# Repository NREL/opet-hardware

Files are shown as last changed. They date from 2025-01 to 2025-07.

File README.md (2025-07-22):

# OPET hardware introduction
This repository contains everything relating to the hardware of the OPET device.  If you are looking for the firmware or software repositories, links are below:

[OPET Firmware](https://github.com/NREL/opet-firmware)

[OPET Control Software](https://github.com/NREL/opet-control)

## Feature summary
- OPET (Open-source Photovoltaic Electrical Tool) is used for performance measurements of solar photovoltaic (PV) devices in the field under natural sunlight or in the lab under artificial light
- Its primary use is in research and development of solar cells and modules, specifically in reliability and durability research of PV devices
- Some features and functions include:
    - IV curve measurements with linear or cosine distributed measurement points
    - PV device active loading at open circuit voltage (V<sub>oc</sub>), short circuit current (I<sub>sc</sub>) and maximum power point (P<sub>mp</sub>)
    - Bias power supply to overcome series resistance in contact wires for I<sub>sc</sub> measurements and loading
    - PV voltage input in five ranges from 1V to 100V
    - PV current input ranges
        - Low current version, six current ranges from 1.1mA to 340mA
        - High current version, six current ranges from 50mA to 15A
    - IO ports for I2C and SPI temperature sensor Arduino extension boards
    - Integrated fan control

## Safety note

## General Specifications
- Input Power
    - Amplifier supply: 24 Vdc nominal (19 Vdc -- 29 Vdc)
        - Low Current Version 250mA maximum
        - High Current Version 150mA maximum
    - RS485 supply: 5 Vdc nominal (4.75 Vdc -- 5.25 Vdc), 200mA maximum for entire bus
    - High current OPET PV bias supply: 2.0 Vdc to 5.5 Vdc, 15A maximum
    - Fan relay power feedthrough: 24 Vdc recommended (\<150 Vdc, \<100 Vac), 2A maximum
- Electrical Protection
    - Amplifier supply: 30 Vdc, fused with 500 mA ceramic fast blow 20 mm x 5 mm fuse
    - RS485 supply: 5.6 Vdc, requires external 250 mA inline fuse for RS485 bus
    - PV voltage: 100 V on all ranges
    - PV current, High current OPET PV bias supply: 100 V on all ranges
    - High current OPET PV bias supply and PV current:
        - 15 A on all ranges, fused with 16 A \>100 Vdc rated 32 mm x 6.3 mm ceramic fuse
    - Low current OPET PV current:
        - 340 mA on all ranges, fused with 500 mA \>100 Vdc rated 20 mm x 5 mm ceramic fast blow fuse
        - It should survive at 15A current spike with the correct fuse installed in case a full-sized module is connected to a low current OPET by accident, but not tested yet
- Environment
    - Temperature
        - Operation 0 °C to 40 °C
        - Storage -30 °C to 60 °C
    - Relative humidity (non-condensing)
        - Operating 0 °C to 28 °C \<90 %
        - Operating 28 °C to 40 °C \<80 %
        - Storage -30 °C to 60 °C \<95%
    - Altitude
        - Operating up to 3,000 Meters (limited by PCB track spacing according to ICP 2221)
        - Storage up to 12,000 Meters
- Remote interface
    - RS485 half-duplex, 200k baud, up to 32 devices per bus

## Electrical Specifications

### PV Voltage Specifications
- Maximum input: 100V on any range
- Measurement method: 16bit SAR ADC
- Input characteristics:
    - Range defines the nominal range value; system is designed with a \>3% overrange margin
    - Eff. ADC resolution describes the ADCs effective performance, \~15bit
        - The 1V range is effectively a part of the 4.2V range
    - Accuracy is given as ± (% of measurement + % of range), detailing scale and offset uncertainty respectively
        - The total uncertainty of a measurement is defined as $U = \ \sqrt{{U_{Scale}}^{2} + {U_{Offset}}^{2}}$
        - Uncertainty is reported with a 95% confidence (k=2)
        - Uncertainty is largely based on theoretical calculations, albeit care has been taken to include every conceivable source, these may not be fully representative, design requirement was a total uncertainty of less than 0.1%
        - Uncertainty given excludes external calibration uncertainty, calibration should be caried out using suitable equipment that does not add a significant contribution
    - Input impedance describes the total voltage terminal resistance path when voltage is within selected measurement range, the resulting current leakage is corrected on current measurements taken
    
| Range | Eff. ADC resolution |    Accuracy     | Input Impedance |
|:-----:|:-------------------:|:---------------:|:---------------:|
| 1.0 V |       0.14 mV       | 0.011% + 0.031% |    1.100 MΩ     |
| 4.2 V |       0.14 mV       | 0.011% + 0.007% |    1.100 MΩ     |
| 10 V  |       0.32 mV       | 0.019% + 0.007% |    0.163 MΩ     |
| 30 V  |       0.97 mV       | 0.025% + 0.007% |    0.115 MΩ     |
| 100 V |       3.23 mV       | 0.038% + 0.007% |    0.104 MΩ     |

### PV Current Specifications
- Maximum input:
    - High Current OPET: 15A on any range
    - Low current OPET: 340mA on any range
- Measurement method: 16bit SAR ADC
- Input characteristics:
    - Range defines the nominal range value; system is designed with a \>3% overrange margin
    - Eff. ADC resolution describes the ADCs effective performance, \~15bit
    - Accuracy is given as ± (% of measurement + % of range), detailing scale and offset uncertainty respectively
        - The total uncertainty of a measurement is defined as $U = \ \sqrt{{U_{Scale}}^{2} + {U_{Offset}}^{2}}$
        - Uncertainty is reported with a 95% confidence (k=2)
        - Uncertainty is largely based on theoretical calculations, albeit care has been taken to include every conceivable source, these may not be fully representative, design requirement was a total uncertainty of less than 0.1%
        - Uncertainty given excludes external calibration uncertainty, calibration should be caried out using suitable equipment that does not add a significant contribution
- Current measurements are corrected for leakage through the PV voltage channel impedance

#### Low current OPET
|  Range  | Eff. ADC resolution |    Accuracy     | Shunt Resistance |
|:-------:|:-------------------:|:---------------:|:----------------:|
| 1.1 mA  |       35.1 nA       | 0.050% + 0.017% |     23.20 Ω      |
| 3.2 mA  |      104.4 nA       | 0.049% + 0.008% |     23.20 Ω      |
| 11.0 mA |       360 nA        | 0.056% + 0.017% |      2.26 Ω      |
|  33 mA  |       1072 nA       | 0.055% + 0.008% |      2.26 Ω      |
| 110 mA  |       3.70 µA       | 0.053% + 0.018% |      0.22 Ω      |
| 340 mA  |      11.01 µA       | 0.052% + 0.008% |      0.22 Ω      |

#### High current OPET
|  Range   | Eff. ADC resolution |    Accuracy     | Shunt Resistance |
|:--------:|:-------------------:|:---------------:|:----------------:|
| 50.0 mA  |      1629.0 nA      | 0.059% + 0.017% |      0.50 Ω      |
| 150.0 mA |      4843.6 nA      | 0.054% + 0.008% |      0.50 Ω      |
| 500.0 mA |      16290 nA       | 0.055% + 0.017% |      0.05 Ω      |
| 1500 mA  |      48436 nA       | 0.058% + 0.008% |      0.05 Ω      |
| 5000 mA  |      162.90 µA      | 0.057% + 0.017% |      0.01 Ω      |
| 15000 mA |      484.36 µA      | 0.058% + 0.008% |      0.01 Ω      |

# Preparing for Operation
- The OPET circuit board needs to be prepared and set-up for operation
- First an overview of the OPET printed circuit board (PCB) is given
- it is detailed how to wire up and power the system
- enclosure with air-cooling requirements and recommendations are also given

## Circuit Board overview and outline

### Low current OPET PCB overview


### High current OPET PCB overview


### Dimensions
- Both, low and high current OPET boards have the exact same PCB with a different set of components
- hence, board dimensions and the positions of the mounting holes are the same


### Connectors
- All of the side connectors on the OPET are pluggable screw or clamp terminals
    - This is to reduce the strain on the PCB when connecting a cable
- CAUTION:
    - Always disconnect the pluggable connector before connecting/removing wires from the plug
    - Not removing the plug puts pressure onto the board from the top when tightening or loosening the screw that bends the PCB and can cause micro-cracking in components
    - Early failure especially in capacitors and changes in performance with calibration drift may be result
- The labelling of connectors is done on the front and the backside of the PCB, so that it is easily readable in different mounting positions
- Labelling is as following, see section in 2.2 for further details:
    - Amp PWR: 24V & GND amplifier power supply input
    - RS485: two RS485 communication ports with A & B data lines and 5V & GND supply input
        - One for input and one for feedthrough to the next unit
    - Fan: standard molex fan connector powered from the 24V Amp PWR input
    - FT: fan power feedthrough relay connection to be used with an externally powered fan
    - SPI & I2C ports: these are expansion sockets to connect a breakout module with RTD or thermocouple sensor
    - PV Curr: for the current carrying pair of the 4-wire contacts to the PV device
    - PV Volt: for the voltage sensing pair of the 4-wire contacts to the PV device
    - Bias PWR: for the bias power supply input on the high current OPET version
    - MOSFET: for the external driver MOSFET if not onboard
    - NTC2: for the external driver MOSFET temperature sensor

### Headers, Jumpers and Fuses
- Two headers are positioned in the left area of the PCB with following function:
    - ISP: is the 6-pin In-System Programmer port used to program the microcontroller on the board
    - JTAG: the Joint Test Action Group port is used for debugging and programming of the onboard microcontroller
        - This port is normally disabled to make room for the RS485 address selection
        - Is very useful for updating and finetuning the controller code
        - Make sure ADR jumpers are removed before using this port
    - Both ports follow the standard AVR pin-out and can be connected directly to a programmer
        - an Atmel-ICE programmer has been used during the design of OPET


- The ADR jumper row is used to set the RS485 address of the OPET device

### Fuses
- WARNING:
    - Always replace fuses on the OPET with the correct type and specifications
    - Using the wrong fuse may cause no-functioning protection in case of a fault, which can lead damaged equipment and/or personal injury
- OPET has 2 fuses onboard
    - All Are ceramic fuses, they are used for an improved DC and current braking capability rating
- FS1: amplifier power input fuse
    - 20x5 mm ceramic fuse, 500 mA ≥50 Vdc rated, fast action
    - ideally use "Littelfuse 0216.500MXP"
    - this fuse can blow if the amplifier input voltage is too high and the 30 V Zehner diode protects the input to the DC/DC converters
- FS4: PV device current protection fuse
    - Low current OPET: 20x5 mm ceramic fuse, 250 mA ≥100 Vdc rated, fast action
        - Important to use "Littelfuse 0216.250MXP"
    - High current OPET: 6.3x32 mm ceramic fuse, 15-20 A ≥100 Vdc rated
        - use "Littelfuse 0314015.MXP" 15A fuse or Littelfuse 0314020.MXP" 20A fuse, or "Schurter 8020.5023" 16A fuse
        - IMPORTANT:
            - this fuse is likely to get very hot (\>80°C) when operating at or near maximum specified currents (15 A)
            - hence its recommended to use a 20 A fuse when the PV load is likely to reach near to 15 A current flow, this reduces heat on the OPET board and degradation of the fuse over time (early fuse failure)

### Indicators
- OPET board has 3 indicator LEDs in the left side:
    - Green: Power indicator
        - Indicates if the Microcontroller is receiving 5V input voltage
    - Orange: Output enabled indicator
        - In principle this LED indicates if the output of the OPET is
            - Enabled, driver controller in active voltage regulation
            - Disabled, driver controller inactive with high impedance input (V<sub>oc</sub>) at PV current input
        - Indicator shows enabled if the power output is requested to be enabled
        - In case of an error (see below error indicator details), the actual output can be high impedance inactive, while the output indicator is still active
            - this is to indicate that as soon as the error clears the output will become active automatically
        - in V<sub>oc</sub> load mode, the output is also inactive high impedance, while the OPET shows an output active indicator
            - this is to show that the output is requested to be active and ready to measure IV curves in between V<sub>oc</sub> loading at high impedance
    - Red: Error active indicator
        - This LED will become active when the OPET has detected an error during operation
        - Some errors will lead to a temporal disabling of the output if the output was requested to be on to start with, others are indicative only
        - The type of error that is active can be queried when requesting load measurement data or reading the status byte (see 4.3.1.1 for more details)
        - In case of voltage or current ADC measurement errors the error LED is likely to flash constantly or briefly, if observing this:
            - Check measurement ranges
            - Check stability of PI controller
            - Check noise level on the current and voltage signals
            - Check PV device connection polarity

## Electrical connections and set-up

### Amplifier Supply
- The AMP supply input of the OPET is used to power the electronics on the PCB
    - On the Low current OPET version it also sources the Bias voltage through a DC/DC converter connected to the AMP supply input
- The nominal voltage of the input is 24V, with an input range of 19-29 V
    - Can be powered with a 24V battery system, however it needs additional battery management and protection as OPET will not automatically switch off when it reaches under-or over-voltage conditions
- Normal current draw is \~60-75 mA if the output is off
    - Low current OPET versions can have up to \~150 mA current draw at maximum current PV load
- The AMP input has following protections:
    - reverse polarity protection
    - over-voltage protection with a 30V Zehner diode
    - and fused with a 500 mA 20x5 mm ceramic fuse,
        - Ceramic fuse is used to reach an improved DC and current braking capability rating
- The AMP input is also Isolated, to the rest of the electronics excluding the fan using isolated DC/DC controllers
    - This reduces problems occurring due to ground shifting when connecting multiple OPET boards on to one supply
- OPETs have an AMP input filter and DC/DC output filter to reduce noise impact, it is however still recommended to use a high-quality supply with low output ripple noise
- When selecting a power supply, it is also important to make sure its maximum capacitive load requirement is above the input capacitance of the OPET PCBs (\~25µF) multiplied by the number of boards connected

### RS485 Bus Communication
- OPET incorporates an isolated half-duplex RS485 port for communication
- Up to 32 devices can be connected to a single RS485 bus
    - OPET is designed for 32 devices on one bus, this has not been fully tested
- OPET has two connectors for RS485 onboard
    - one for the RS485 input and one to feedthrough to the next device on the bus
    - both can be used for either function
- To connect OPET devices to a computer it is recommended to use a USB to RS485 converter, devices have been tested with the FTDI USB-RS485-WE-1800-BT USB to RS485 converter
- Following connection schematic is used to connect the OPET systems to a RS485 bus



#### Bus Power Supply
- Since an isolated RS485 system is used to electrically separate multiple devices from each other and to reduce interference the RS485 must be powered with an external 5V supply with a minimum current output of 250mA
- This is in many cases is already incorporated into the USB-RS485 converter, such as with the recommended converter given in the section above, if not, the RS485 bus can be powered with an external supply
- power is feed through from device to device in the same way as the data lines
- The input voltage must be within the range of 4.75 V and 5.25 V for the RS485 transceiver on the OPET to work correctly
- The input is reverse polarity protected and has a 5.6V Zehner clamping diode to protect against short time overvoltage spikes at the input to the transceiver.
    - Short time: maximum a few seconds dependent on the input voltage, fault current and heat on the Zehner diode
    - A 250 mA fuse in line with the RS485 bus power is recommended to enhance protection
    - Current may be electronically limited when using a USB to RS485 converter with 5V output powered via USB, a fuse is in this case not needed
    - If an external dedicated power supply is used to power the RS485 bus is advised to use a 250 mA series fuse in the 5V line to the first OPET device.
- Since up to 32 OPET devices are connected in series via the feedthrough connections and hence the total length of the bus cable can be long, it is advised to use as large wire gauge as possible to reduce the voltage losses within the bus to less than 0.15 V on a 5 V bus input to stay within the transceiver operating voltage range from the first to the last device on the bus while still allowing for input voltage tolerances
    - Total length: keep as short as possible to reduce losses
    - Wire gauge: OPET connectors accept 20 to 26 AWG, the thicker the conductor the lower the losses

#### RS485 bus termination and biasing
- To improve communication reliability and quality the RS485 bus uses termination and biasing techniques
- RS485 bus termination is used to reduce/eliminated signal reflection at the end and start points of the bus
    - Done by connecting a 120 Ω resistor at each end of the bus in series from data A to data B
    - The recommended FTDI USB to RS485 converter has this incorporated and just needs shorting of the dedicated wires to enable 120 Ω termination at the bus start point
    - The OPET device does not have a termination onboard and a external 120 Ω resistor should be connected to the feedthrough terminal (whichever connector is not used yet) of the last device in line from contact A to B
    - a termination is typically not needed on very short bus line (\<2m) with only a few devices connected
- RS485 bus biasing is used to keep the voltage potential of the data lines A & B apart from each other when the bus is inactive and none of the devices on the bus are transmitting
    - Too little biasing can cause accidental start pulses on the bus and interrupt communication
    - OPET has biasing resistors included that allow for optimal biasing at 32 devices on the bus (68 kΩ per device, \~2.1 kΩ in total with 32 devices on the bus)
    - External biasing when not using 32 devices is usually not needed, however if using an old RS485 transceiver (USB to RS485 converter or similar) this may be need when communicating to only a few devices
    - If communication is in the above case unreliable / not working at all do following:
        - At the start of the RS485 bus before the first device connect
            - a 10 kΩ resistor from Data A to 5V
            - and a 10 kΩ resistor from Data B to GND

#### How to set the hardware bus address 
- The bus address of each OPET device is determined by hardware addressing on the PCB, which is the jumper header next to the RS485 connectors
- Any device can have any bus address independent of its position on the actual RS485 bus as long as the address is not used twice
    - In case of using a bus address twice, communication to this address will fail as two devices will start using the bus at the same time
    - OPET does not recognise bus communication collisions when multiple devices communicate at the same time, nor does OPET have an auto-addressing function
- To set the address of a OPET do the following:
    - Insert a jumper into the positions required that make up the desired address number in binary code
    - Address = 1\*x + 2\*x + 4\*x + 16\*x, while x represents a 1 if jumper is inserted and 0 if not
    - Addressing starts at 0 and ends at 31, for a maximum of 32 devices
- IMPORTANT:
    - Remove the Address jumpers when using the OPET in debug mode with a JTAG
    - The default address when debugging is "1" `A:...`
    - See the software programming notes for more details

### FAN and FT connectors
- The FAN connection uses a standard molex connector for computer fans
    - It is powered by the AmpPWR supply; hence it is recommended to use a 24V fan
    - Fan power is not in-line with the amp power fuse
    - up to 2A current rating limited by the control relay
- The FT connector is a relayed power feedthrough that closes when the fan is controlled on
    - This can be used to power fans from an additional power supply
    - Voltage rating is \<150 Vdc, \<100 Vac, 2A current rating
- The fan control is a simple on/off control
    - controlled either manually or automatically (by default) by temperature and load power hysteresis that can be configured in the EEPROM (see section 5.3.19)

### SPI and I2C ports
- The SPI and I2C ports can be used to connect breakout board to the OPET
- Main use is to connect temperature sensor breakout boards
- OPET currently supports following boards:
    - Adafruit MCP9600 I2C Thermocouple Amplifier
        - Connected directly to J8
    - Adafruit MAX31865 RTD PT100 or PT1000 Amplifier
        - Connected directly to J18
    - See section [XXX]{.mark} for details on how to configure a temperature sensor breakout board
- IMPORTANT:
    - Switch off the OPET before disconnecting or connecting a breakout board
- The pinout description is given on the OPET PCB and below

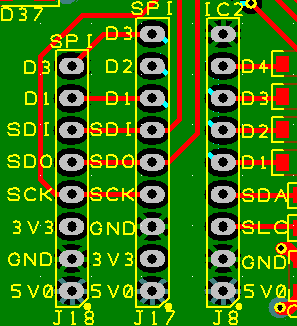
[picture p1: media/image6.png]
Pinout description of the OPET I2C and SPI expansion ports


### High Current OPET Driver Stage and Voltage Bias Supply
- WARNING:
    - Do not connect/ disconnect test leads from the bias voltage supply to the OPET when it is under load or when the PV device is placed under light and supplying electricity
    - Do not connect/ disconnect test leads from the driver MOSFET to the OPET when it is under load or when PV device is placed under light and supplying electricity
    - Cover the module with cardboard or similar to remove light input and power off OPET when connecting / disconnecting test leads
- The driver MOSFET and bias voltage protection diodes are mounted externally on a heatsink due to the additional heat produced from the larger load and current flow
- The bias voltage supply is also external, as it needs to supply the same current as the PV device
- Due to the low load current and total heat dissipation, those components are internal on the low current OPET versions
- The bias voltage supply is connected with two protective diodes:
    - One diode in series for reverse polarity protection
    - And one diode in parallel to bypass the voltage supply in case it is switched off or cannot keep up with the PV device load current
    - The "onsemi FFPF30UP20STU" diode is recommended
        - due to its low forward voltage even at high currents (typically 0.9 V at 15 A)
        - due to its isolated case, meaning no thermal pads are needed, only thermal paste, which improves thermal conductivity significantly
- the requirements of the bias voltage power supply are as follows:
    - output voltage minimum 0 V (just shorted) to maximum 6 V
        - dependent on the length of the cable to the PV device and the maximum current flowing
        - the losses on the cables, protection diode and within the OPET board must be lower than the voltage bias supply to be able to measure directly at I­<sub>sc</sub> load
        - if the bias voltage is too low, the OPET system will not be able to get to I<sub>sc</sub> loading at the PV device, which may be less of a problem with high voltage PV modules, but will cause problems when measuring wafer sized solar cells
    - output current of at least the expected maximum current of the PV device
        - a reserve headroom of \~30% is recommended
        - if the PV load current exceeds the bias voltage supply current, the current is bypassed through the protective diodes, meaning the OPET will not be able to reach I<sub>sc</sub> load
    - use a power supply with the lowest noise possible, as this will improve measurement quality and stability
        - unlike the low-current OPET version with bias supply on-board, the high current version has no bias voltage supply filter
        - a noisy voltage supply will cause noisier PV load measurements
    - when using a single bias voltage supply for multiple high current OPETs:
        - connect them using a star connection directly to the power supply terminals, as this will reduce voltage loss and reduce board to board noise coupling
        - use protective diodes for each board separately, to prevent PV load power flow from one board to another
- The driver MOSFET is connected to the MOSFET input of the OPET
    - The "IXYS IXFN132N50P3" MOSFET is recommended
        - Due to its high current and voltage load capability
        - Due to its large metal base footprint and ability to sink up to 1.5kW of power
        - Due to its isolated base, meaning no thermal pad is needed, only thermal paste, which improves thermal conductivity significantly
    - Is its recommended to use one driver MOSFET only, but multiple can theoretically be used
        - This can increase the practical maximum load
        - however, comes with additional difficulties, see end of this section for recommendations
- A NTC thermal sensor is additionally mounted onto the MOSFET and connected to the OPET, to make sure the system does not overheat
    - Recommended NTC is the "EPCOS B57703M0103A018"
        - Has through hole mounting and comes wire leaded
- Refer to section 2.3.3 for details and requirements to mount the MOSFET and diodes on a heatsink
- Wire requirements are as follows:
    - MOSFET and Bias voltage connectors accept 12 to 24 AWG
    - The thicker the conductor the lower the losses induced by wire resistance and current flow
    - The MOSFET should be connected using the shortest wiring possible, as long cables may introduce high stray capacitance and inductance on the MOSFET gate that reduce driver stability
    - The Bias Voltage protection diodes should also be as near as possible to the OPET, but this requirement is less important
- Following connections need to be made to connect the driver MOSFET and bias voltage with protection diodes:


- Using multiple driver MOSFETs (untested):
    - Use the same type of MOSFET for all
        - Need to be able to sink the current and voltage each, as per datasheet
    - Need to be mounted onto the same heatsink with as good as possible thermal coupling
        - Temperature differences can cause a thermal runaway that cause the hottest MOSFET to carry even more load, heating it further, possibly leading to failure
        - If one MOSFET overheats and fails, all are likely to fail in a cascading failure
        - Thermal coupling can reduce the imbalance between MOSFETs significantly
    - MOSFETs need to have each a separate gate resistor of \~100 Ω (needs testing)
    - MOSFETs must be wired with equal length cables to OPET in a star configuration
        - This reduces imbalance due to series resistance in cables
    - Ideally test the on-resistance of all MOSFETs and use those with most similar on-resistance
        - So called binning
        - Reduces imbalance due to series resistance
    - NTC must be mounted to the MOSFET that is most likely to get hottest (may need additional testing)
    - Below is a diagram of wiring multiple driver MOSFETs to the high-curent OPET



### PV device Connections
- WARNING:
    - Do not connect/ disconnect test leads from the PV device to the OPET when it is under load, or it is in placed under light and supplying electricity
    - Cover the module with cardboard or similar to remove light input when connecting / disconnecting test leads
- PV device connections are made using 4 wires, 2 for the PV device current and two for the PV device voltage sense
    - The pair of current wires carry the current load with low impedance
    - The pair of voltage sense wires have a high input impedance at the OPET and therefore sense the PV voltage without additional current induced voltage losses
    - the voltage is measured at the PV device compensating for losses due to long test leads
- Wire requirements are as follows:
    - PV current connector accepts 12 to 24 AWG
        - the PV current cables should be as short as possible
        - the shorter the lower the losses and bias voltage requirements, the less noise pick-up and the better the stability
    - PV voltage connector accepts 16 to 28 AWG
        - The PV voltage cable should be shielded 2 core to reduce noise pick-up
        - Cable shield should be connected to S (Shield) of the PV volt connector



## Enclosure and cooling
- The printed circuit board (PCB) needs to be housed in an electrically safe enclosure that adequately protects from electric shock and personal injury
- Furthermore, forced air cooling is required for reliable operation within specifications

### Enclosure
- Ideally a metal housing should be used with earth grounding for safety and to reduce signal noise influences
- Mounting of the board can be done vertically in PCB guiderails or horizontally using the mounting holes
- System can be mounted in 19" rack units with multiple units next to each other
- See PCB design notes for mounting hole positions

### Circuit board air cooling
- Active cooling and ventilation of the PCB is required especially when operating the OPETs at high PV device current / power, it has following impact on the system:
    - it improves measurement stability as the board and shunt resistor heatsink temperatures are lower and vary less with PV device load current and power
    - it improves reliability the driver MOSFET and other components
    - it reduces aging drift in the shunt resistors and thus increases stability
- The low current OPET can be used without air cooling if the total power of the PV device does not exceed \~3W
    - cooling should be used above 3W and is a must above \~5W, as otherwise the heat sink will get too hot and trigger the thermal cut-off
- the high current OPETs need separate cooling for the circuit board and for the heatsink with the driver MOSFET and protective diodes
    - high PV currents induce heat on the PV current protection fuse and on the shunt resistors
    - the driver MOSFET carries the electrical load of the PV device and thus must be operated with a good heatsink (see the following section)
- the Airflow should be from front to back of the OPET boards or from bottom to top
    - this makes sure that the heatsink of the shunt resistor is cooled first and secondly the drive MOSFET heatsink or PV current fuse
    - basically, air needs to flow first past measurement critical components and then past power electronics, so that measurement components do not get unnecessarily heated

### High current OPET driver MOSFET and diode cooling
- due to the high current and power potentially going through the high current OPET boards, the driver MOSFET and the bias voltage protection diodes are external from the PCB
- those must be mounted onto a suitable heatsink that is able to take the maximum predicted power from the PV device plus the power from the bias voltage supply
- total estimated power can be calculated as follows:

$$P_{total} = P_{MP} + (V_{bias} - V_{Diode} - V_{cable})*\ I_{MP}$$
- cooling option can either be water or air cooling
- the best cooling option depends on the maximum power requirements
    - with 100 V and 15 A measurement range, theoretically a 1.5kW PV load can be connected
        - Is unlikely practically possible with a PV device
        - a single driver MOSFET load set-up of any kind will probably go off in smoke at this point
    - the maximum load depends mostly on the thermal resistance path from the junction of the driver MOSFET to the heat removing medium (Water, Air)
    - the maximum MOSFET junction temperature should be well below its allowed maximum for reliability (maximum \~100 °C for at 150 °C maximum allowed operation temperature)
    - the temperature of the heat removing air/water influence maximum power as well
- it is important to take care when mounting the MOSFET and protection diodes
- the MOSFET should be mounted as following:
    - in the centre of the heatsink with high grade thermal compound in between heatsink and MOSFET
    - do not use thermal pads, as they have lower thermal conductivity and thus can cause excessive heat at the MOSFET that can reduce lifetime or burn it instantly
        - the recommended MOSFET "IXYS IXFN132N50P3" has an isolated metal base, hence additional electrical isolation is not needed
    - mount the thermistor temperature sensor (NTC) directly onto the MOSFET with its mounting screws that go into the heatsink
        - the NTC is the lifeline of the driver MOSFET as it means the OPET can monitor the case temperature and shut power of before damage occurs
        - the NTC head must be mounted between the screw head and MOSFET base
        - Do not mount the NTC between the heatsink and MOSFET, as this will cause a thermal gap and certain death of the MOSFET
- the diodes (recommended "onsemi FFPF30UP20STU") should also be mounted at a distance to the MOSFET using thermal compound
    - thermal pads are not needed due to an isolated TO-220F case
- a suitable heatsink for air cooling is for example the "Fisher Electronik LA 17/150 24V or LA 17/200 24V ", were the 24 Vdc fan option should work best
    - it is estimated that this heatsink should allow for a PV load of \~350 W based on a total thermal resistance of 0.20C/W, reaching a MOSFET junction temperature of \~100 °C at 25 °C air temperature
        - 0.07 °C/W for heatsink, 0.083 °C/W MOSFET junction to case, 0.05 °C/W MOSFET case to heatsink
    - Estimated 12 A maximum current with a 2 Vdc bias voltage remaining after diode and cable losses, causing 24W additional heat at MOSFET
    - It remains to be tested in real operating conditions, as the total thermal resistance may be too optimistic, due to the relatively small surface area of the MOSFET connecting to the heatsink

## Turning Power-On
- After adhering to the endless list of requirements, warnings & cautions, boxing it all in and hocking up the cables, one should be able to just power it up and get going
- The OPET system boots up and is ready to go in less than a second
    - WARNING:
        - it may also go up in flames just as fast as it boots
            - if it is powered by direct mains voltage
            - if it is not wired correctly
- To power up the OPET only amp power is needed, there is no strict on/off button, it powers up as soon as power is connected and will stay powered up until the input power is removed
    - If a power button is desired, a switch can be added to the positive pole of the AMP input power line

# Calibration

## Introductions
- Following sections detail the calibration and adjustment procedure for the OPET systems
- Care should be taken to make sure measurements are done without introducing additional errors
- Furthermore, take note that the high current and low current versions of the OPETs require different current calibration connections!
- The easiest way to calibrate the OPET devices is to use the calibration software tool developed for it, however this only works with a Fluke / Wavetek 9100 calibrator at the moment
- WARNING: make sure the calibration set-up is electrically touch prove and save, as the calibration will source voltages over 42 Vdc into the OPET devices, which can result in personal injuries or death if accidently touched

## Requirements
- A current and voltage calibrator should be used to calibrate the OPET system
- For this a controllable power supply in combination with a digital multimeter can also be used
- Important is that the measurement uncertainty of the calibration system is lower than that of the OPET devices
    - The total uncertainty is the OPET (see section 1.4) uncertainty combined with the calibration uncertainty
    - if calibration uncertainty is high, the resulting uncertainty after calibration and adjustment will degrade OPET total uncertainty
- calibrations have been down using a Fluke / Wavetek 9100 calibrator, for which also an easy-to-use calibration tool was developed
    - this requires a GPIB connection the calibrator and the computer
    - and a LabVIEW 2018 32bit runtime install to run the executable (or a licence to open/run the VI files)
- WARNING, it is important to shield the OPET during calibration:
    - Foremostly, to make sure it is electrically safe and high voltage parts cannot be touched
    - Secondly, a metal case to reduce measurement noise
        - An earth wire may be used to connect to a metal case
        - The shield input at the PV voltage terminals can be used connect case and OPET
        - it may take a little tinkering to get the best results with lowest noise
- otherwise, all you need is luck, patients and suitable connections with calibration cables

## Calibrator Connections

### Voltage
- Voltage calibrations are carried out by making a 2-wire connection between the calibrator voltage terminals and the PV voltage input terminals
- Since the OPET voltage input is differential to provide 4-wire PV measurements, the negative PV terminal and the shield input of the PV voltage connector should be bridged
    - This should reduce signal noise significantly
- Following connection diagram was used for high and low current OPET devices:


### Current
- Current calibration connections are not made via the PV current input terminals on the OPET devices due to the driver MOSFET and the bias voltage supply that is in line with the PV current terminals
    - Instead, current calibration is done with connections going directly over the shunt resistors current path, bypassing the drive MOSFET and the bias voltage supply
    - Using the PV current terminals may be possible, but has not been done as it may risk damaging the calibrator
- CAUTION:
    - Low and high current OPET devices use different current calibration connections
    - Do not use the low current connections for calibrating OPETs with more than 150mA current
    - Doing so will likely result in damaging the OPET

### Low Current systems
- Following connection diagram is used for the low current OPET devices

- The connections for calibrating the low current devices are done from the current outputs of the calibrator to the OPET device
    - Negative pole: PV voltage connector shield (S) terminal
    - Positive pole: MOSFET connector source (S) terminal
- CAUTION: do not use the low current connections for high current calibrations above 350mA
    - This may result in damaging the OPET PCB by burning off the voltage terminal shield track which cannot handle high currents, even for short times

### High Current systems
- Following connection diagram is used for the hight current OPET devices
- This configuration can also be used for low current OPET devices if the bias connector is installed or one connects directly to the PCB at the Bias PWR GND terminal


- The connections for calibrating the high current devices are done from the current outputs of the calibrator to the OPET device
    - Negative pole: Bias power connector ground (GND) terminal
    - Positive pole: MOSFET connector source (S) terminal
- The bias voltage supply ground connector can handle high currents
    - hence this terminal is used for high current OPETs
    - it can also be used on low current units, but the connector may not be installed

# Making OPETs

## PCB Design Files
The provided files were created using [RS Design Spark](https://www.rs-online.com/designspark/pcb-software) software.  Schematics of individual systems are broken out individually.  The PCB design is unified between both the HC and LC versions of the OPET.  Custom library components are also provided.

[OPET PCB Design Files](OPET_PCB_Design_Files)

Note that bills of materials for board components are located in the [OPET Manufacture Files](OPET_Manufacture_Files) folder.

## Manufacture Files
If your goal is to just have some OPET tools manufactured, all the necessary files are included in the [OPET Manufacture Files](OPET_Manufacture_Files) folder.  These files should include everything a PCB manufacturing house needs to fabricate the PCBs and acquire and assemble components.

- **OPET - Gerber** Gerber manufacturing files.
- **OPET - BOM Hardware** List of mechanical hardware options for assembling OPETs.  This includes things like screws, nuts and thermal pads or paste.
- **OPET - BOM HC** Bill of materials for the high current OPET model.
- **OPET - BOM LC** Bill of materials for the low current OPET model.
- **OPET - CPL Component Placement List** Contains the positions and orientations of components.  Will be required for PCB assembly.
- **OPET - PCB Manufacturing Notes** Includes notes about copper weight, board specifications and other notes that a manufacturer will need.

# Disclaimer

DISCLAIMER: NREL/ALLIANCE FOR SUSTAINABLE ENERGY, LLC/DOE DISCLAIM ALL WARRANTIES, EXPRESS OR IMPLIED, INCLUDING THE WARRANTIES OF MERCHANTABILITY OR FITNESS FOR A PARTICULAR PURPOSE, AND MAKES NO WARRANTY AS TO THE ACCURACY, COMPLETENESS, OR USEFULNESS OF ANY INFORMATION PROVIDED HEREIN. USE OF THIS PACKAGE IS AT THE USER’S OWN RISK.

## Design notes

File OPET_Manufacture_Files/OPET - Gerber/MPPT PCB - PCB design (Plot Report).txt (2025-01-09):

Plot Report
-----------

Report Written:     Wednesday, May 15, 2024
Project Path:       D:\BLISS_DATA\7_WORK_SPACE\NREL MPPT tracer\Hardware\OPET PCB\MPPT PCB - Project.prj
Design Path:        D:\BLISS_DATA\7_WORK_SPACE\NREL MPPT tracer\Hardware\OPET PCB\MPPT PCB - PCB design.pcb
Design Title:       
Created:            03/04/2020 02:22:14
Last Saved:         15/05/2024 23:10:25
Editing Time:       25039 min
Units:              inches (precision 4)

Device Settings
===============

Gerber Settings
===============

    Leading zero suppression.
    G01 assumed throughout.
    Line termination <*> <CR> <LF>.
    3.5 format absolute inches.

    Format commands defined in Gerber file.
    Aperture table defined in Gerber file.
    Hardware arcs allowed.

Drill Settings
==============

    Excellon Format 2
    Format 3.5 absolute in inches.
    Zero suppression Leading

Plots Output
============

    Plot Job: "D:\BLISS_DATA\7_WORK_SPACE\NREL MPPT tracer\Hardware\OPET PCB\MPPT PCB - PCB design.mop"

Gerber Output
=============

D:\BLISS_DATA\7_WORK_SPACE\NREL MPPT tracer\Hardware\OPET PCB\Gerber\MPPT PCB - PCB design - Top Silkscreen.gbr

    Layers:
    ------------------
    Top Silkscreen

    D-Code Shape  (thou)
    -----------------------
    D10    Round 5.00
    D76    Round 10.00
    D77    Round 12.00

Gerber Output
=============

D:\BLISS_DATA\7_WORK_SPACE\NREL MPPT tracer\Hardware\OPET PCB\Gerber\MPPT PCB - PCB design - Top Copper.gbr

    Layers:
    --------------
    Top Copper

    D-Code Shape  (thou)
    -----------------------------------------------
    D10    Round 5.00
    D11    Round 23.62
    D12    Round 19.69
    D13    Round 15.75
    D14    Round 35.43
    D15    Round 62.99
    D16    Round 74.80
    D17    Round 39.37
    D18    Round 118.11
    D19    Round 11.81
    D70    Round 236.22
    D78    Round 8.66
    D79    Rectangle 19.69 X 82.68  Rotation 90
    D80    Rectangle 19.69 X 82.68
    D81    Rectangle 23.62 X 94.49  Rotation 90
    D82    Rectangle 86.61 X 110.24
    D83    Rectangle 62.99 X 125.98  Rotation 90
    D84    Rectangle 23.62 X 90.55
    D85    Rectangle 39.37 X 51.18
    D86    Rectangle 39.37 X 51.18  Rotation 90
    D87    Rectangle 59.06 X 118.11
    D88    Rectangle 15.75 X 61.02  Rotation 90
    D89    Rectangle 11.02 X 61.02  Rotation 90
    D90    Rectangle 23.62 X 90.55  Rotation 90
    D91    Rectangle 59.06 X 118.11  Rotation 90
    D92    Rectangle 23.62 X 70.87  Rotation 90
    D93    Rectangle 31.50 X 47.24
    D94    Rectangle 55.12 X 70.87  Rotation 90
    D95    Rectangle 55.12 X 70.87
    D96    Rectangle 47.24 X 62.99  Rotation 90
    D97    Rectangle 47.24 X 62.99
    D98    Rectangle 78.74 X 78.74  Rotation 90
    D99    Rectangle 23.62 X 74.80  Rotation 90
    D100   Rectangle 31.50 X 39.37  Rotation 90
    D101   Rectangle 31.50 X 39.37
    D102   Rectangle 78.74 X 141.73
    D103   Rectangle 23.62 X 51.18  Rotation 90
    D104   Rectangle 23.62 X 94.49
    D105   Rectangle 43.31 X 51.18  Rotation 90
    D106   Rectangle 55.12 X 62.99
    D107   Rectangle 23.62 X 74.80
    D108   Rectangle 23.62 X 70.87
    D109   Rectangle 94.49 X 165.35
    D110   Rectangle 55.12 X 149.61
    D111   Rectangle 86.61 X 110.24  Rotation 90
    D112   Rectangle 94.49 X 165.35  Rotation 90
    D113   Rectangle 70.87 X 78.74  Rotation 90
    D114   Rectangle 51.18 X 70.87
    D115   Rectangle 70.87 X 78.74
    D116   Rectangle 51.18 X 70.87  Rotation 90
    D117   Rectangle 62.99 X 125.98
    D118   Rectangle 78.74 X 157.48
    D119   Rectangle 31.50 X 47.24  Rotation 90
    D120   Rectangle 78.74 X 78.74
    D121   Rectangle 23.62 X 51.18
    D150   Round 25.00
    D151   Round 59.06
    D152   Round 80.31
    D153   Round 70.87
    D154   Round 78.74
    D155   Round 157.48
    D156   Round 137.80
    D157   Round 98.43
    D158   Round 55.12
    D159   Round 37.40
    D160   Round 82.68
    D161   Oval 51.18 X 78.74  Rotation 90

Gerber Output
=============

D:\BLISS_DATA\7_WORK_SPACE\NREL MPPT tracer\Hardware\OPET PCB\Gerber\MPPT PCB - PCB design - Top Copper (Resist).gbr

    Layers:
    --------------
    Top Copper

    D-Code Shape  (thou)
    ------------------------------------------------
    D71    Round 246.22
    D20    Round 128.11
    D21    Round 90.31
    D22    Round 80.87
    D23    Round 88.74
    D24    Round 72.99
    D25    Round 167.48
    D26    Round 147.80
    D27    Round 108.43
    D28    Round 84.80
    D29    Round 65.12
    D72    Round 47.40
    D73    Round 92.68
    D74    Oval 61.18 X 88.74  Rotation 90
    D122   Rectangle 29.69 X 92.68  Rotation 90
    D123   Rectangle 29.69 X 92.68
    D124   Rectangle 33.62 X 104.49  Rotation 90
    D125   Rectangle 96.61 X 120.24
    D126   Rectangle 72.99 X 135.98  Rotation 90
    D127   Rectangle 33.62 X 100.55
    D128   Rectangle 49.37 X 61.18
    D129   Rectangle 49.37 X 61.18  Rotation 90
    D130   Rectangle 69.06 X 128.11
    D131   Rectangle 25.75 X 71.02  Rotation 90
    D132   Rectangle 21.02 X 71.02  Rotation 90
    D133   Rectangle 33.62 X 100.55  Rotation 90
    D134   Rectangle 69.06 X 128.11  Rotation 90
    D135   Rectangle 33.62 X 80.87  Rotation 90
    D136   Rectangle 41.50 X 57.24
    D137   Rectangle 65.12 X 80.87  Rotation 90
    D138   Rectangle 65.12 X 80.87
    D139   Rectangle 57.24 X 72.99  Rotation 90
    D140   Rectangle 57.24 X 72.99
    D141   Rectangle 88.74 X 88.74  Rotation 90
    D142   Rectangle 33.62 X 84.80  Rotation 90
    D143   Rectangle 41.50 X 49.37  Rotation 90
    D144   Rectangle 41.50 X 49.37
    D145   Rectangle 88.74 X 151.73
    D146   Rectangle 33.62 X 61.18  Rotation 90
    D147   Rectangle 33.62 X 104.49
    D148   Rectangle 53.31 X 61.18  Rotation 90
    D149   Rectangle 65.12 X 72.99
    D162   Rectangle 33.62 X 84.80
    D163   Rectangle 33.62 X 80.87
    D164   Rectangle 104.49 X 175.35
    D165   Rectangle 65.12 X 159.61
    D166   Rectangle 96.61 X 120.24  Rotation 90
    D167   Rectangle 104.49 X 175.35  Rotation 90
    D168   Rectangle 80.87 X 88.74  Rotation 90
    D169   Rectangle 61.18 X 80.87
    D170   Rectangle 80.87 X 88.74
    D171   Rectangle 61.18 X 80.87  Rotation 90
    D172   Rectangle 72.99 X 135.98
    D173   Rectangle 88.74 X 167.48
    D174   Rectangle 41.50 X 57.24  Rotation 90
    D175   Rectangle 88.74 X 88.74
    D176   Rectangle 33.62 X 61.18
    D177   Round 49.37

Gerber Output
=============

D:\BLISS_DATA\7_WORK_SPACE\NREL MPPT tracer\Hardware\OPET PCB\Gerber\MPPT PCB - PCB design - Top Copper (Paste).gbr

    Layers:
    --------------
    Top Copper

    D-Code Shape  (thou)
    -----------------------------------------------
    D138   Rectangle 15.69 X 78.68  Rotation 90
    D139   Rectangle 15.69 X 78.68
    D140   Rectangle 19.62 X 90.49  Rotation 90
    D141   Rectangle 82.61 X 106.24
    D142   Rectangle 58.99 X 121.98  Rotation 90
    D143   Rectangle 19.62 X 86.55
    D144   Rectangle 35.37 X 47.18
    D145   Rectangle 35.37 X 47.18  Rotation 90
    D146   Rectangle 55.06 X 114.11
    D147   Rectangle 11.75 X 57.02  Rotation 90
    D148   Rectangle 7.02 X 57.02  Rotation 90
    D149   Rectangle 19.62 X 86.55  Rotation 90
    D162   Rectangle 55.06 X 114.11  Rotation 90
    D163   Rectangle 19.62 X 66.87  Rotation 90
    D164   Rectangle 27.50 X 43.24
    D165   Rectangle 51.12 X 66.87  Rotation 90
    D166   Rectangle 51.12 X 66.87
    D167   Rectangle 43.24 X 58.99  Rotation 90
    D168   Rectangle 43.24 X 58.99
    D169   Rectangle 74.74 X 74.74  Rotation 90
    D170   Rectangle 19.62 X 70.80  Rotation 90
    D171   Rectangle 27.50 X 35.37  Rotation 90
    D172   Rectangle 27.50 X 35.37
    D173   Rectangle 74.74 X 137.73
    D174   Rectangle 19.62 X 47.18  Rotation 90
    D175   Rectangle 19.62 X 90.49
    D176   Rectangle 39.31 X 47.18  Rotation 90
    D177   Rectangle 51.12 X 58.99
    D178   Rectangle 19.62 X 70.80
    D179   Rectangle 19.62 X 66.87
    D180   Rectangle 90.49 X 161.35
    D181   Rectangle 51.12 X 145.61
    D182   Rectangle 82.61 X 106.24  Rotation 90
    D183   Rectangle 90.49 X 161.35  Rotation 90
    D184   Rectangle 66.87 X 74.74  Rotation 90
    D185   Rectangle 47.18 X 66.87
    D186   Rectangle 66.87 X 74.74
    D187   Rectangle 47.18 X 66.87  Rotation 90
    D188   Rectangle 58.99 X 121.98
    D189   Rectangle 74.74 X 153.48
    D190   Rectangle 27.50 X 43.24  Rotation 90
    D191   Rectangle 74.74 X 74.74
    D192   Rectangle 19.62 X 47.18
    D193   Round 58.99
    D194   Round 35.37

Gerber Output
=============

D:\BLISS_DATA\7_WORK_SPACE\NREL MPPT tracer\Hardware\OPET PCB\Gerber\MPPT PCB - PCB design - Documentation.gbr

    Layers:
    -----------------
    Documentation

    D-Code Shape  (thou)
    -----------------------
    D10    Round 5.00

Gerber Output
=============

D:\BLISS_DATA\7_WORK_SPACE\NREL MPPT tracer\Hardware\OPET PCB\Gerber\MPPT PCB - PCB design - Inner 1 Top.gbr

    Layers:
    -------------
    Gnd Plane

    D-Code Shape  (thou)
    -----------------------------------------
    D10    Round 5.00
    D11    Round 23.62
    D12    Round 19.69
    D13    Round 15.75
    D14    Round 39.37
    D15    Round 11.81
    D16    Round 74.80
    D17    Round 35.43
    D18    Round 62.99
    D19    Round 236.22
    D70    Round 118.11
    D71    Round 80.31
    D20    Round 70.87
    D21    Round 78.74
    D22    Round 157.48
    D23    Round 137.80
    D24    Round 98.43
    D25    Round 55.12
    D26    Round 37.40
    D27    Round 82.68
    D28    Oval 51.18 X 78.74  Rotation 90

Gerber Output
=============

D:\BLISS_DATA\7_WORK_SPACE\NREL MPPT tracer\Hardware\OPET PCB\Gerber\MPPT PCB - PCB design - Inner 2 Bot.gbr

    Layers:
    -------------
    Vcc Plane

    D-Code Shape  (thou)
    -----------------------------------------
    D10    Round 5.00
    D11    Round 23.62
    D12    Round 19.69
    D13    Round 15.75
    D14    Round 39.37
    D15    Round 11.81
    D16    Round 74.80
    D17    Round 35.43
    D18    Round 62.99
    D19    Round 236.22
    D70    Round 118.11
    D71    Round 80.31
    D20    Round 70.87
    D21    Round 78.74
    D22    Round 157.48
    D23    Round 137.80
    D24    Round 98.43
    D25    Round 55.12
    D26    Round 37.40
    D27    Round 82.68
    D28    Oval 51.18 X 78.74  Rotation 90
    D29    Round 25.00
    D72    Round 59.06

Gerber Output
=============

D:\BLISS_DATA\7_WORK_SPACE\NREL MPPT tracer\Hardware\OPET PCB\Gerber\MPPT PCB - PCB design - Bottom Copper.gbr

    Layers:
    -----------------
    Bottom Copper

    D-Code Shape  (thou)
    -----------------------------------------
    D10    Round 5.00
    D11    Round 23.62
    D12    Round 19.69
    D13    Round 15.75
    D14    Round 39.37
    D15    Round 11.81
    D16    Round 74.80
    D17    Round 35.43
    D18    Round 62.99
    D19    Round 236.22
    D70    Round 118.11
    D71    Round 80.31
    D20    Round 70.87
    D21    Round 78.74
    D22    Round 157.48
    D23    Round 137.80
    D24    Round 98.43
    D25    Round 55.12
    D26    Round 37.40
    D27    Round 82.68
    D28    Oval 51.18 X 78.74  Rotation 90
    D29    Round 25.00
    D72    Round 59.06

Gerber Output
=============

D:\BLISS_DATA\7_WORK_SPACE\NREL MPPT tracer\Hardware\OPET PCB\Gerber\MPPT PCB - PCB design - Bottom Copper (Resist).gbr

    Layers:
    -----------------
    Bottom Copper

    D-Code Shape  (thou)
    -----------------------------------------
    D73    Round 246.22
    D74    Round 128.11
    D75    Round 90.31
    D76    Round 80.87
    D77    Round 88.74
    D78    Round 72.99
    D79    Round 167.48
    D80    Round 147.80
    D81    Round 108.43
    D82    Round 84.80
    D83    Round 65.12
    D84    Round 47.40
    D85    Round 92.68
    D86    Oval 61.18 X 88.74  Rotation 90

Gerber Output
=============

D:\BLISS_DATA\7_WORK_SPACE\NREL MPPT tracer\Hardware\OPET PCB\Gerber\MPPT PCB - PCB design - Bottom Copper (Paste).gbr

    Layers:
    -----------------
    Bottom Copper

    D-Code Shape  (thou)
    -----------------------

NC Drill Output
===============

D:\BLISS_DATA\7_WORK_SPACE\NREL MPPT tracer\Hardware\OPET PCB\Gerber\MPPT PCB - PCB design - Drill Data - [Through Hole].drl

    Output:
    ---------------------------
    Plated Round Drill Holes
    Plated Slots

    Tool  Size           Count   ID
    --------------------------------------
    T001  0.01969 inches 389   A
    T002  0.02559 inches 10    J
    T003  0.03150 inches 50    I
    T004  0.03937 inches 90    B
    T005  0.04724 inches 29    F
    T006  0.05512 inches 3     E
    T007  0.06299 inches 11    D
    T008  0.07874 inches 6     G
    T009  0.11811 inches 6     H
    T010  0.13780 inches 12    C
    --------------------------------------
    Total                606
    --------------------------------------

D:\BLISS_DATA\7_WORK_SPACE\NREL MPPT tracer\Hardware\OPET PCB\Gerber\MPPT PCB - PCB design - Drill Data - [Through Hole] (Unplated).drl

    Output:
    -----------------------------
    Unplated Round Drill Holes
    Unplated Slots

    Tool  Size           Count   ID
    --------------------------------------
    T001  0.05118 inches 1     K
    --------------------------------------
    Total                1
    --------------------------------------

Gerber Output
=============

D:\BLISS_DATA\7_WORK_SPACE\NREL MPPT tracer\Hardware\OPET PCB\Gerber\MPPT PCB - PCB design - Drill Ident Drawing - [Through Hole].gbr

    Layers:
    ------------------
    [Through Hole]

Drill Ident Drawing
===================

    Drill Plated Size Shape ID
    -----------------------------------
    20    Y      100  Round A
    39    Y      100  Round B
    138   Y      100  Round C
    63    Y      100  Round D
    55    Y      100  Round E
    47    Y      100  Round F
    79    Y      100  Round G
    118   Y      100  Round H
    31    Y      100  Round I
    26    Y      100  Round J
    51           100  Round K

    D-Code Shape  (thou)
    -----------------------
    D10    Round 5.00
    D87    Round 100.00

Gerber Output
=============

D:\BLISS_DATA\7_WORK_SPACE\NREL MPPT tracer\Hardware\OPET PCB\Gerber\MPPT PCB - PCB design - Board Outline.gbr

    Layers:
    ------------------
    Board Outlines

    D-Code Shape  (thou)
    -----------------------
    D10    Round 5.00

Gerber Output
=============

D:\BLISS_DATA\7_WORK_SPACE\NREL MPPT tracer\Hardware\OPET PCB\Gerber\MPPT PCB - PCB design - Bottom Silkscreen.gbr

    Layers:
    ---------------------
    Bottom Silkscreen

    D-Code Shape  (thou)
    -----------------------
    D88    Round 10.00

End Of Report.

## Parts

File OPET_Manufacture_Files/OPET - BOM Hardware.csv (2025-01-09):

OPET Hardware
HC Model
 | Location | Quantity | Dimension | Part Number | Vendor
 | T4 | 1 | M3x0.5 16mm | 91292A115 | McMaster Carr
 | T4 | 2 | M3 Washer | 98689A112 | McMaster Carr
 | T4 | 1 | M3 Locknut | 93625A100 | McMaster Carr
 | T4 | 1 | Thermal paste for diode (2 legged component) | 860-60G | Digikey
 | T4 | 1 | Thermal pad for MosFET (3 legged component) | 2195N4 | McMaster Carr
 | RS1 | 1 | M3x0.5 16mm | 91292A115 | McMaster Carr
 | RS1 | 2 | M3 Washer | 98689A112 | McMaster Carr
 | RS1 | 1 | M3 Locknut | 93625A100 | McMaster Carr
 | RS1 | 1 | Thermal paste for Resistor (4 legged component) | 860-60G | Digikey
 | RS1 | 1 | Thermal pad for MosFET (3 legged component) | 2195N4 | McMaster Carr
 | VR2 | 1 | M3x0.5 12mm | 91292A114 | McMaster Carr
 | VR2 | 2 | M3 Washer | 98689A112 | McMaster Carr
 | VR2 | 1 | M3 Locknut | 93625A100 | McMaster Carr
LC Model
 | T4 | 1 | M3x0.5 12mm | 91292A114 | McMaster Carr
 | T4 | 2 | M3 Washer | 98689A112 | McMaster Carr
 | T4 | 1 | M3 Locknut | 93625A100 | McMaster Carr
 | T1 | 1 | M3x0.5 12mm | 91292A114 | McMaster Carr
 | T1 | 2 | M3 Washer | 98689A112 | McMaster Carr
 | T1 | 1 | M3 Locknut | 93625A100 | McMaster Carr
 | T1 | 1 | Thermal pad | 2195N4 | McMaster Carr
 | VR2 | 1 | M3x0.5 12mm | 91292A114 | McMaster Carr
 | VR2 | 2 | M3 Washer | 98689A112 | McMaster Carr
 | VR2 | 1 | M3 Locknut | 93625A100 | McMaster Carr

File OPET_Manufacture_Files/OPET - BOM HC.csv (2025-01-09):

Component Description | QTY | Ref Des | Mfg P/N # | Manufacturer | Package
CAP ALUM POLYMR 82UF 20% 25V SMD | 2 | C1,C2 | APXJ250ARA820MF80G | United Chemi-Con | 6.3mm SM Can
CAP CER 0.1UF 50V X7R 0805 | 61 | C10,C101,C102,C103,C104,C11,C110,C111,C114,C115,C119,C123,C126,C13,C14,C18,C19,C21,C22,C26,C28,C29,C30,C32,C33,C34,C35,C36,C38,C39,C40,C41,C45,C46,C47,C48,C51,C52,C53,C54,C55,C56,C60,C61,C62,C64,C65,C72,C73,C76,C8,C84,C85,C86,C87,C88,C89,C9,C96,C97,C99 | 08055C104KAT2A | KYOCERA AVX | 0805
not populated! | 33 | C100,C106,C107,C108,C109,C127,C57,C92,C93,C94,D10,D16,J14,J16,J17,J18,J8,R105,R129,R156,R175,R176,R22,R6,R88,R89,R89,R92,RS4,RT1,RT2,RT3,T7 |  |  | 0
CAP CER 1UF 50V X7R 0805 | 14 | C105,C12,C124,C128,C129,C15,C16,C20,C23,C24,C31,C50,C74,C98 | CL21B105KBFNFNE | Samsung Electro-Mechanics | 0805
CAP CER SMD 0805 .01UF 100V X7R | 4 | C116,C49,C75,C90 | C0805C103K1RAC7210 | KEMET | 0805
CAP CER 0.022UF 100V X7R 0805 | 1 | C117 | CC0805KRX7R0BB223 | YAGEO | 0805
CAP CER 0.047UF 100V X7R 0805 | 1 | C118 | CL21B473KCFNNNE | Samsung Electro-Mechanics | 0805
CAP CER 200PF 50V NPO 0805 | 3 | C122,C68,C69 | CC0805JRNPO9BN201 | YAGEO | 0805
CAP TANT 10UF 20% 16V 1411 | 4 | C125,C17,C25,C27 | TPSB106M016R0800 | KYOCERA AVX | 1411
CAP ALUM 15UF 20% 50V SMD | 1 | C4 | 865080643007 | Würth Elektronik | 6.3mm SM Can
CAP CER 6800PF 50V X7R 0805 | 4 | C42,C43,C44,C77 | 08055C682KAT2A | KYOCERA AVX | 0805
CAP CER 0.33UF 50V X7R 0805 | 3 | C5,C6,C7 | CL21B334KBFNFNE | Samsung Electro-Mechanics | 0805
CAP CER 10PF 50V C0G/NP0 0805 | 2 | C58,C59 | C0805C100K5GAC7800 | KEMET | 0805
CAP CER 4700PF 100V X7R 0805 | 1 | C63 | 885012207120 | Würth Elektronik | 0805
CAP CER 100PF 100V C0G/NP0 0805 | 2 | C66,C67 | CL21C101JCANNNC | Samsung Electro-Mechanics | 0805
CAP CER 1500PF 50V C0G/NP0 0805 | 2 | C70,C71 | C0805C152J5GAC7800 | KEMET | 0805
CAP ALUM POLY 100UF 20% 63V SMD | 1 | C78 | APD1012101M063R | KYOCERA AVX | 10mm SM Can
CAP TANT 10UF 10% 25V 1411 | 2 | C81,C82 | TAJB106K025TNJ | KYOCERA AVX | 1411
CAP CER 4.7PF 50V C0G/NP0 0805 | 2 | C91,C95 | VJ0805A4R7BXACW1BC | Vishay Vitramon | 0805
DIODE ZENER 30V 1W PMDS | 1 | D1 | PTZTE2530A | Rohm Semiconductor | SOD-106-2
DIODE SCHOTTKY 30V 200MA SOD323 | 8 | D12,D13,D17,D27,D28,D34,D36,D38 | BAT54WS-TP | Micro Commercial Co | SOD-323
DIODE ARR GEN PUR 80V 215MA SSD3 | 4 | D18,D19,D3,D4 | BAV199HMT116 | Rohm Semiconductor | SOT-23-3
DIODE GEN PURP 200V 2A DO214AA | 1 | D2 | ES2D | onsemi | DO-214AA
DIODE ARRAY SCHOTTKY 40V SOT23-3 | 3 | D20,D21,D33 | BAS40-04-7-F | Diodes Incorporated | SOT-23-3
DIODE ZENER 5.6V 500MW SOD123 | 4 | D22,D23,D35,D37 | BZT52C5V6-TP | Micro Commercial Co | SOD-123
SOD-323, SWITCHING | 3 | D24,D25,D26 | BAS116WS-AU_R1_000A1 | Panjit International Inc. | SOD-323
DIODE ZENER 16V 1W SOD123FL | 6 | D29,D30,D5,D6,D7,D8 | DFLZ16-TP | Micro Commercial Co | SOD-123FL
DIODE GEN PURP 200V 30A TO220F | 3 | Ex_D1,Ex_D2,T4_B | FFPF30UP20STU | onsemi | TO-220
MOSFET N-CH 500V 112A SOT227B | 1 | Ex_MF1 | IXFN132N50P3 | IXYS | Screw
NTC Thermistors NTC Thermistor M 703/10 K/A 18 2% | 1 | Ex_NTC2 | B57703M0103A018 | EPCOS / TDK | TH 2p wire
FUSEHOLDER BLOCKS - PCB - CLIP C | 1 | FS1_A | 696101000002 | Würth Elektronik | TH 2p 22.6mm
FUSE CERAMIC 500MA 250VAC 5X20MM | 1 | FS1_B | 5HF 500-R | Bel Fuse Inc. | 20x5mm
FUSE CLIP CARTRIDGE 1KV 30A PCB | 2 | FS4_A,FS4_B | 01220088Z | Littelfuse Inc. | TH
Cartridge Fuses 250V 20A Fast Acting | 1 | FS4_C | 0314020.MXP | Littelfuse Inc. | 6.3x32mm
2 Position Terminal Block Header, Male Pins, Shrouded (4 Side) 0.200" (5.08mm) 90°, Right Angle - Through Hole | 3 | J10_A,J11_A,J1_A | TBP01R1-508-02BE | CUI Devices | TH 2pin 5.08mm
2 Position Terminal Block Plug, Female Sockets 0.200" (5.08mm) - 180° Free Hanging (In-Line) | 3 | J10_B,J11_B,J1_B | TBP01P1-508-02BE | CUI Devices | TH 2pin 5.08mm Plug
3 Position Terminal Block Header, Male Pins, Shrouded (4 Side) 0.200" (5.08mm) 90°, Right Angle - Through Hole | 1 | J12_A | TBP01R1-508-03BE | CUI Devices | TH 3pin 5.08mm
3 Position Terminal Block Plug, Female Sockets 0.200" (5.08mm) 180° Free Hanging (In-Line) | 1 | J12_B | TBP01P1-508-03BE | CUI Devices | TH 3pin 5.08mm Plug
TERM BLOCK HDR 2POS 90DEG 3.5MM | 2 | J13_A,J15_A | 284512-2 | TE Connectivity | TH 2pin 3.5mm
TERM BLOCK PLUG 2POS STR 3.5MM | 2 | J13_B,J15_B | 284506-2 | TE Connectivity AMP Connectors | TH 2pin 3.5mm Plug
Connector Header Through Hole 10 position 0.100" (2.54mm) | 1 | J2 | 10129381-910002BLF | Amphenol ICC (FCI) | TH 2x5pin 2.54mm
Pluggable Terminal Blocks PTSM 0,5/ 4-HH-2,5 THR R32 | 2 | J3_A,J5_A | 1778641 | Phoenix Contact | TH 4pin 2.5mm
Pluggable Terminal Blocks PTSM 0,5/ 4-P-2,5 | 2 | J3_B,J5_B | 1778858 | Phoenix Contact | TH 4pin 2.5mm Plug
CONN HEADER VERT 6POS 2.54MM | 1 | J4 | 10129381-906001BLF | Amphenol ICC (FCI) | TH 2x3pin 2.5mm
PIN HEADER, THR, DUAL ROW, 1.27 | 1 | J6 | PR20B05VBDN | METZ CONNECT USA Inc. | TH 2x5pin 1.27mm
Connector Header Through Hole 4 position 0.100" (2.54mm) | 1 | J7 | 47053-3000 | Molex | SIL 4pin 2.54mm
TERM BLOCK HDR 3POS 90DEG 3.5MM | 1 | J9_A | 0395021003 | Molex | TH 3pin 3.5mm
TERM BLOCK PLUG 3POS STR 3.5MM | 1 | J9_B | 0395000003 | Molex | TH 3pin 3.5mm Plug
FERRITE BEAD 1 KOHM 1206 1LN | 2 | L4,L5 | BLM31KN102SN1L | Murata Electronics | 1206
FIXED IND 12UH 2A 125 MOHM SMD | 1 | L6 | SRR4828A-120M | Bourns Inc. | 1919
FIXED IND 100UH 700MA 600MOHM SM | 2 | L8,L9 | SRR4828A-101M | Bourns Inc. | 1919
LED GREEN CLEAR 0805 SMD | 1 | LED1 | 150080GS75000 | Würth Elektronik | 0805
LED YELLOW CLEAR 0805 SMD | 1 | LED2 | 5988150107F | Dialight | 0805
LED RED CLEAR 0805 SMD | 1 | LED3 | 150080RS75000 | Würth Elektronik | 0805
THERMISTOR NTC 10KOHM 3940K 0805 | 1 | NTC1 | NTCS0805E3103JHT | Vishay Beyschlag/Draloric/BC Components | 0805
RES 200K OHM 1% 1/8W 0805 | 5 | R1,R2,R3,R4,R5 | RC0805FR-07200KL | YAGEO | 0805
RES 100 OHM 1% 1/8W 0805 | 28 | R10,R11,R112,R115,R116,R12,R13,R130,R14,R165,R166,R167,R168,R27,R28,R32,R33,R34,R35,R36,R37,R42,R43,R60,R61,R70,R74,R93 | RC0805FR-07100RL | YAGEO | 0805
RES 4.99K OHM 1% 1/8W 0805 | 12 | R100,R106,R107,R108,R114,R136,R155,R171,R64,R65,R66,R67 | AC0805FR-074K99L | YAGEO | 0805
RES 10K OHM 1% 1/8W 0805 | 12 | R101,R102,R103,R110,R111,R137,R21,R71,R96,R97,R98,R99 | RC0805FR-0710KL | YAGEO | 0805
RES 2.49K OHM 1% 1/8W 0805 | 2 | R104,R72 | RC0805FR-072K49L | YAGEO | 0805
RES 20K OHM 1% 1/8W 0805 | 4 | R109,R138,R169,R170 | RC0805FR-0720KL | YAGEO | 0805
RES 3K OHM 1% 1/8W 0805 | 3 | R113,R135,R73 | RMCF0805FT3K00 | Stackpole Electronics Inc | 0805
RES 1K OHM 1% 1/8W 0805 | 29 | R117,R131,R132,R141,R142,R143,R144,R24,R25,R26,R29,R30,R31,R38,R39,R40,R41,R46,R47,R51,R53,R54,R55,R56,R57,R62,R63,R87,R90 | RC0805FR-071KL | YAGEO | 0805
RES 49.9K OHM 1% 1/8W 0805 | 13 | R118,R119,R133,R134,R157,R158,R161,R162,R163,R164,R7,R8,R9 | AC0805FR-0749K9L | YAGEO | 0805
RES 10K OHM 0.1% 1/8W 0805 | 2 | R120,R121 | RN73R2ATTD1002B25 | KOA Speer Electronics, Inc. | 0805
RES 11.5K OHM 1% 1/8W 0805 | 6 | R122,R123,R79,R80,R81,R82 | RC0805FR-0711K5L | YAGEO | 0805
RES 470 OHM 1% 1/8W 0805 | 13 | R124,R125,R126,R127,R128,R139,R140,R159,R160,R23,R75,R76,R77 | RC0805FR-07470RL | YAGEO | 0805
RES 1 OHM 1% 1/4W 1206 | 4 | R145,R146,R44,R45 | RMCF1206FT1R00 | Stackpole Electronics Inc | 1206
RES 20 KOHMS 0.1% 0.4W 1206 | 5 | R149,R150,R151,R152,R153 | RQ73C2B20KBTD | TE Connectivity Passive Product | 1206
RES 4.12 KOHMS 0.1% 1/5W 0805 | 1 | R15 | RQ73C2A4K12BTD | TE Connectivity Passive Product | 0805
RES 20 OHM 1% 1/8W 0805 | 2 | R154,R78 | RC0805FR-0720RL | YAGEO | 0805
RES 15.4 KOHMS 0.1% 1/5W 0805 | 1 | R16 | RQ73C2A15K4BTD | TE Connectivity Passive Product | 0805
RES 68.1 KOHMS 0.1% 1/5W 0805 | 1 | R17 | RQ73C2A68K1BTD | TE Connectivity Passive Product | 0805
RES 100K OHM 1% 1/4W 1206 | 5 | R172,R173,R19,R20,R94 | RMCF1206FT100K | Stackpole Electronics Inc | 1206
RES SMD 1M OHM 0.1% 1/4W 1206 | 1 | R18 | RP73D2B1M0BTDF | TE Connectivity Passive Product | 1206
RES 100K OHM 1% 1/8W 0805 | 4 | R48,R50,R52,R95 | RC0805FR-13100KL | YAGEO | 0805
RES 4.3K OHM 1% 1/8W 0805 | 1 | R49 | RC0805FR-074K3L | YAGEO | 0805
RES 976 OHMS 0.1% 1/5W 0805 | 1 | R58 | RQ73C2A976RBTD | TE Connectivity Passive Product | 0805
RES 324 OHMS 0.1% 1/5W 0805 | 1 | R59 | RQ73C2A324RBTD | TE Connectivity Passive Product | 0805
RES 68K OHM 1% 1/8W 0805 | 2 | R68,R69 | RC0805FR-1368KL | YAGEO | 0805
RES 560 OHM 1% 1/8W 0805 | 2 | R83,R84 | RC0805FR-07560RL | YAGEO | 0805
RES 100 KOHMS 0.1% 1/5W 0805 | 1 | R85 | RN73C2A100KBTD | TE Connectivity Passive Product | 0805
RES 1 KOHMS 0.1% 1/5W 0805 | 1 | R86 | RQ73C2A1K0BTD | TE Connectivity Passive Product | 0805
Through Hole Metal Foil Resistor, FHR 4-2321 Series, 0.005 ohm, 3 W, - 1%, 300 V RoHS Compliant: Yes | 1 | RS1_A | FHR 4-2321 0R005 S 1% Q | POWERTRON | TH
MOSFET N CH 40V 195A TO220 | 2 | RS1_B,T4_A | IRFB7430PBF | Infineon Technologies | TO-220
Thermal Insulator, Insulating Kit, Mica, TO-220, Mica, 1 kV, 0.1 mm | 3 | RS1_C,T4_C,T4_D | MK3306/TG | MULTICOMP | 0
HEATSINK TO-218,TO-220,TO-247 | 1 | RS1_D | RA-T2X-51E | Ohmite | TH
50mΩ, 2512 (6432M) SMD Resistor ±1% 3 W @ 95°C - VMS-R050-1.0-U | 1 | RS2 | VMS-R050-1.0-U | Isabellenhutte | 2512
500mΩ, 2512 (6432M) SMD Resistor ±1% 3 W | 1 | RS3 | VMS-R500-1.0-U | Isabellenhutte | 2512
Telecom Relay DPDT (2 Form C) Through Hole | 4 | SW1,SW2,SW3,SW4 | 6-1462037-6 | TE Connectivity Potter & Brumfield Relays | TH
MOSFET N-CHANNEL 30V 32A 8SOIC | 2 | T2,T3 | SQ4182EY-T1_BE3 | Vishay Siliconix | SOIC-8
Heat Sinks High Efficiency Heat Sink For Vertical Board Mounting for TO-220, 50.8mm Height | 1 | T4_E | 637-20ABPE | Wakefield-Vette | 0
MOSFET N-CH 30V 350MA SOT23 | 2 | T5,T6 | DMN63D8L-7 | Diodes Incorporated | SOT-23
MOSFET P-CH 20V 3.1A SOT23 | 1 | T9 | DMP2170U-7 | Diodes Incorporated | SOT-23
IC MCU 8BIT 128KB FLASH 44TQFP | 1 | U1 | ATMEGA1284-AUR | Microchip Technology | TQFP-44
IC GATE DRVR LOW-SIDE 8SOIC | 2 | U10,U11 | MIC4127YME-TR | Microchip Technology | SOIC-8
IC OPAMP GP 2 CIRCUIT 8SOIC | 6 | U12,U19,U23,U24,U25,U28 | OP2177ARZ | Analog Devices Inc. | SOIC-8
IC FF D-TYPE SNGL 1BIT SOT23-6 | 1 | U13 | SN74LVC1G175DBVT | Texas Instruments | SOT-23-6
Bipolar Motor Driver Power MOSFET - TSOT-23-6 | 4 | U14,U15,U31,U32 | MP6513GJ-P | Monolithic Power Systems Inc. | TSOT23-6
IC I/O EXPANDER I2C 16B 24SOIC | 1 | U16 | PCA9555D,118 | NXP | WSOIC-24
IC MUX CMOS SINGLE 8CH 16-SOIC | 1 | U17 | DG408LEDY-T1-GE3 | Vishay Siliconix | SOIC-16
IC OPAMP GP 1 CIRCUIT 8SOIC | 2 | U18,U20 | OP1177ARZ-REEL7 | Analog Devices Inc. | SOIC-8
ISO RS485/422 0.2MBPS 2.5KVRMS | 1 | U2 | ISO3082DWR | Texas Instruments | WSOIC-16
Multiplexer Switch ICs 36V, Low-Capacitance Analog Multiplexer | 2 | U21,U30 | MUX508IDR | Texas Instruments | SOIC-16
IC SWITCH SPDT 8SOIC | 1 | U26 | MAX4659ESA+T | Maxim Integrated | SOIC-8
IC VREF SERIES 0.1% 8SOIC 4.096V | 1 | U27 | MCP1501T-40E/SN | Microchip Technology | SOIC-8
16 Bit Digital to Analog Converter 1 8-VSSOP | 1 | U3 | DAC8550IBDGKT | Texas Instruments | VSSOP-8
Analog to Digital Converters - ADC 16-Bit, 500ksps/250ksps Serial ADCs in Tiny 10-Pin Packages | 1 | U4 | MAX11163EUB+T | Maxim Integrated | umax-10
IC VREF SERIES 0.12% 8SOIC 4.096V | 1 | U5 | REF198FSZ-REEL | Analog Devices Inc. | SOIC-8
IC INST AMP 1 CIRCUIT 8SOIC | 2 | U6,U8 | AD8221ARZ-R7 | Analog Devices Inc. | SOIC-8
IC MUX CMOS DUAL 4CH 16-SOIC | 1 | U9 | DG409LEDY-T1-GE3 | Vishay Semiconductors | SOIC-16
IC REG LINEAR 5V 100MA 8SO | 1 | VR1 | L78L05CD13TR | STMicroelectronics | SOIC-8
Linear Voltage Regulators Precision 1.5A Reg 5V Output Dual Gauge | 1 | VR2_A | L7805ACV-DG | STMicroelectronics | TO-220
Heat Sinks Wave-Solder, Heat Sink, TO220, 14.5x12.7x19.1mm, Vertical/Horizontal, No Tab | 1 | VR2_B | 230-75AB | Wakefield-Vette | TO-220
IC REG LINEAR -5V 100MA 8SO | 1 | VR3 | L79L05ACD13TR | STMicroelectronics | SOIC-8
DC DC CONVERTER +/-15V 3W | 1 | VR4 | TMR 3-2423WI | Traco Power | TH
Crystal, 16 MHz, SMD, 3.2mm x 2.5mm, 10 ppm, 9 pF, 10 ppm, ABM8 Series | 1 | XTAL1 | ABM8-16.000MHZ-9-B1U-T | ABRACON | SMD 3.2mm x 2.5mm

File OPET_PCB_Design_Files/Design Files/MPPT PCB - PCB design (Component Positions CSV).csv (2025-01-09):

Name | Component | Side | Place X | Place Y | Rotation
U6 | AD8221ARZ | Top | 5.815 | 0.4016 | 90
U8 | AD8221ARZ | Top | 5.6378 | 1.689 | 90
U1 | ATmega324P-TQFP | Top | 1.5315 | 2.5866 | 90
J13 | Con_plug_2n_3-50p | Top | 8.8898 | 2.3898 | 90
J15 | Con_plug_2n_3-50p | Top | 0.2047 | 1.7992 | 270
J1 | Con_plug_2n_5-08p | Top | 0.2668 | 4.8425 | 270
J10 | Con_plug_2n_5-08p | Top | 8.8277 | 4.9252 | 90
J11 | Con_plug_2n_5-08p | Top | 8.8277 | 4.3346 | 90
J9 | Con_plug_3n_3-50p | Top | 8.89 | 0.7482 | 90
J12 | Con_plug_3n_5-08p | Top | 8.8277 | 3.641 | 90
J3 | Con_plug_4n_2-50p | Top | 0.2254 | 4.252 | 270
J5 | Con_plug_4n_2-50p | Top | 0.2254 | 3.6811 | 270
J4 | C_AVR_ISP-6 | Top | 1.5354 | 1.7802 | 180
J6 | C_AVR_JTAG_10 | Top | 1.3543 | 3.2119 | 0
C5 | C_Cap_Cera_SMD_2012m | Top | 2.5945 | 3.3346 | 0
C6 | C_Cap_Cera_SMD_2012m | Top | 2.3228 | 3.7756 | 180
C7 | C_Cap_Cera_SMD_2012m | Top | 3.0472 | 3.3346 | 0
C8 | C_Cap_Cera_SMD_2012m | Top | 2.685 | 2.8622 | 180
C9 | C_Cap_Cera_SMD_2012m | Top | 2.0551 | 3.7756 | 180
C10 | C_Cap_Cera_SMD_2012m | Top | 3.0394 | 2.8622 | 180
C11 | C_Cap_Cera_SMD_2012m | Top | 1.5276 | 2.2283 | 180
C12 | C_Cap_Cera_SMD_2012m | Top | 2.0551 | 3.5236 | 180
C13 | C_Cap_Cera_SMD_2012m | Top | 1.5118 | 3.878 | 270
C14 | C_Cap_Cera_SMD_2012m | Top | 0.874 | 3.9291 | 270
C15 | C_Cap_Cera_SMD_2012m | Top | 0.7756 | 3.9291 | 270
C16 | C_Cap_Cera_SMD_2012m | Top | 1.6063 | 3.878 | 270
C18 | C_Cap_Cera_SMD_2012m | Top | 1.937 | 2.563 | 180
C19 | C_Cap_Cera_SMD_2012m | Top | 2.5984 | 1.7283 | 0
C20 | C_Cap_Cera_SMD_2012m | Top | 2.5984 | 1.622 | 0
C21 | C_Cap_Cera_SMD_2012m | Top | 3.0551 | 2.0827 | 270
C22 | C_Cap_Cera_SMD_2012m | Top | 3.0551 | 1.7283 | 90
C23 | C_Cap_Cera_SMD_2012m | Top | 3.1496 | 2.0827 | 270
C24 | C_Cap_Cera_SMD_2012m | Top | 3.1496 | 1.7283 | 90
C26 | C_Cap_Cera_SMD_2012m | Top | 2.7953 | 2.4254 | 90
C28 | C_Cap_Cera_SMD_2012m | Top | 3.2677 | 2.4648 | 270
C29 | C_Cap_Cera_SMD_2012m | Top | 2.8898 | 2.2126 | 180
C30 | C_Cap_Cera_SMD_2012m | Top | 2.8819 | 1.6974 | 0
C31 | C_Cap_Cera_SMD_2012m | Top | 2.8898 | 1.9528 | 180
C32 | C_Cap_Cera_SMD_2012m | Top | 4.2087 | 3.2913 | 270
C33 | C_Cap_Cera_SMD_2012m | Top | 5.563 | 0.2717 | 0
C34 | C_Cap_Cera_SMD_2012m | Top | 5.622 | 0.5945 | 0
C35 | C_Cap_Cera_SMD_2012m | Top | 6.2087 | 1.0906 | 0
C36 | C_Cap_Cera_SMD_2012m | Top | 6.2953 | 0.8465 | 180
C38 | C_Cap_Cera_SMD_2012m | Top | 5.4173 | 1.5197 | 90
C39 | C_Cap_Cera_SMD_2012m | Top | 5.437 | 1.878 | 0
C40 | C_Cap_Cera_SMD_2012m | Top | 5.9685 | 2.0906 | 0
C41 | C_Cap_Cera_SMD_2012m | Top | 6.4724 | 2.1299 | 270
C42 | C_Cap_Cera_SMD_2012m | Top | 6.7008 | 1.5669 | 90
C43 | C_Cap_Cera_SMD_2012m | Top | 6.7008 | 1.9213 | 90
C44 | C_Cap_Cera_SMD_2012m | Top | 6.7008 | 2.2087 | 90
C45 | C_Cap_Cera_SMD_2012m | Top | 6.252 | 2.8031 | 0
C46 | C_Cap_Cera_SMD_2012m | Top | 6.252 | 2.4094 | 0
C47 | C_Cap_Cera_SMD_2012m | Top | 5.7244 | 3.2047 | 180
C48 | C_Cap_Cera_SMD_2012m | Top | 5.8976 | 3.563 | 0
C49 | C_Cap_Cera_SMD_2012m | Top | 5.9134 | 3.2087 | 180
C50 | C_Cap_Cera_SMD_2012m | Top | 6.0472 | 3.4055 | 270
C51 | C_Cap_Cera_SMD_2012m | Top | 5.462 | 2.7756 | 0
C52 | C_Cap_Cera_SMD_2012m | Top | 5.5591 | 0.8189 | 0
C53 | C_Cap_Cera_SMD_2012m | Top | 1.0945 | 2.6063 | 0
C54 | C_Cap_Cera_SMD_2012m | Top | 1.5591 | 2.9803 | 0
C55 | C_Cap_Cera_SMD_2012m | Top | 0.7717 | 2.3661 | 180
C56 | C_Cap_Cera_SMD_2012m | Top | 2.0118 | 0.4724 | 270
C57 | C_Cap_Cera_SMD_2012m | Top | 6.1575 | 0.4016 | 90
C58 | C_Cap_Cera_SMD_2012m | Top | 2.1496 | 2.7362 | 270
C59 | C_Cap_Cera_SMD_2012m | Top | 2 | 2.9094 | 180
C60 | C_Cap_Cera_SMD_2012m | Top | 2.8504 | 1.5236 | 0
C61 | C_Cap_Cera_SMD_2012m | Top | 3.4449 | 1.2638 | 90
C62 | C_Cap_Cera_SMD_2012m | Top | 3.189 | 1.5512 | 0
C63 | C_Cap_Cera_SMD_2012m | Top | 3.0551 | 1.9055 | 270
C64 | C_Cap_Cera_SMD_2012m | Top | 3.1496 | 0.6654 | 90
C65 | C_Cap_Cera_SMD_2012m | Top | 3.5236 | 0.5472 | 270
C66 | C_Cap_Cera_SMD_2012m | Top | 3.2638 | 0.2717 | 180
C67 | C_Cap_Cera_SMD_2012m | Top | 3.315 | 0.9488 | 0
C68 | C_Cap_Cera_SMD_2012m | Top | 3.4606 | 0.374 | 180
C69 | C_Cap_Cera_SMD_2012m | Top | 3.5039 | 0.8465 | 180
C70 | C_Cap_Cera_SMD_2012m | Top | 2.9764 | 0.8071 | 90
C71 | C_Cap_Cera_SMD_2012m | Top | 2.9291 | 0.3346 | 270
C72 | C_Cap_Cera_SMD_2012m | Top | 4.5157 | 0.9409 | 0
C73 | C_Cap_Cera_SMD_2012m | Top | 4.9134 | 1.2638 | 270
C74 | C_Cap_Cera_SMD_2012m | Top | 4.3701 | 1.1378 | 90
C75 | C_Cap_Cera_SMD_2012m | Top | 4.4685 | 1.1378 | 90
C76 | C_Cap_Cera_SMD_2012m | Top | 2.7913 | 1.0276 | 0
C77 | C_Cap_Cera_SMD_2012m | Top | 5.862 | 1.6866 | 270
C80 | C_Cap_Cera_SMD_2012m | Top | 3.5236 | 4.7087 | 90
C84 | C_Cap_Cera_SMD_2012m | Top | 4.0354 | 3.9291 | 270
C85 | C_Cap_Cera_SMD_2012m | Top | 3.6693 | 4.1024 | 90
C86 | C_Cap_Cera_SMD_2012m | Top | 4.185 | 5.0787 | 90
C87 | C_Cap_Cera_SMD_2012m | Top | 4.5512 | 4.8819 | 270
C88 | C_Cap_Cera_SMD_2012m | Top | 5.4449 | 4.8858 | 270
C89 | C_Cap_Cera_SMD_2012m | Top | 5.0669 | 5.0787 | 90
C90 | C_Cap_Cera_SMD_2012m | Top | 3.9252 | 3.7874 | 0
C91 | C_Cap_Cera_SMD_2012m | Top | 3.8386 | 4.2441 | 180
C92 | C_Cap_Cera_SMD_2012m | Top | 4.3465 | 5.2008 | 180
C93 | C_Cap_Cera_SMD_2012m | Top | 4.2992 | 4.7362 | 180
C94 | C_Cap_Cera_SMD_2012m | Top | 5.189 | 4.7362 | 180
C95 | C_Cap_Cera_SMD_2012m | Top | 5.2362 | 5.1929 | 0
C96 | C_Cap_Cera_SMD_2012m | Top | 5.7677 | 4.7323 | 0
C97 | C_Cap_Cera_SMD_2012m | Top | 5.7205 | 5.2087 | 180
C98 | C_Cap_Cera_SMD_2012m | Top | 4.2126 | 1.7677 | 180
C99 | C_Cap_Cera_SMD_2012m | Top | 4.2126 | 1.8622 | 180
C100 | C_Cap_Cera_SMD_2012m | Top | 4.2441 | 2.3425 | 0
C101 | C_Cap_Cera_SMD_2012m | Top | 4.9449 | 2.0157 | 270
C102 | C_Cap_Cera_SMD_2012m | Top | 4.5827 | 2.2677 | 270
C103 | C_Cap_Cera_SMD_2012m | Top | 4.6693 | 1.7559 | 180
C104 | C_Cap_Cera_SMD_2012m | Top | 4.7795 | 2.437 | 180
C105 | C_Cap_Cera_SMD_2012m | Top | 1.9173 | 0.4724 | 270
C110 | C_Cap_Cera_SMD_2012m | Top | 4.7362 | 4.3819 | 270
C111 | C_Cap_Cera_SMD_2012m | Top | 4.6693 | 3.8543 | 180
C114 | C_Cap_Cera_SMD_2012m | Top | 5.626 | 4.3819 | 270
C115 | C_Cap_Cera_SMD_2012m | Top | 5.5551 | 3.8543 | 180
C116 | C_Cap_Cera_SMD_2012m | Top | 5.5276 | 4.4134 | 270
C117 | C_Cap_Cera_SMD_2012m | Top | 5.4291 | 4.4134 | 270
C118 | C_Cap_Cera_SMD_2012m | Top | 5.3307 | 4.4134 | 270
C119 | C_Cap_Cera_SMD_2012m | Top | 5.2323 | 4.4134 | 270
C122 | C_Cap_Cera_SMD_2012m | Top | 3.3228 | 3.7835 | 0
C123 | C_Cap_Cera_SMD_2012m | Top | 1.5079 | 4.3346 | 0
C124 | C_Cap_Cera_SMD_2012m | Top | 1.9921 | 5.3268 | 270
C126 | C_Cap_Cera_SMD_2012m | Top | 3.4449 | 1.4567 | 90
C127 | C_Cap_Cera_SMD_2012m | Top | 4.811 | 5.2953 | 0
C128 | C_Cap_Cera_SMD_2012m | Top | 4.9409 | 1.8189 | 270
C129 | C_Cap_Cera_SMD_2012m | Top | 4.9449 | 2.2205 | 270
C106 | C_Cap_Cera_SMD_3216m | Top | 8.2913 | 0.5551 | 180
C107 | C_Cap_Cera_SMD_3216m | Top | 8.4724 | 4.3307 | 180
C108 | C_Cap_Cera_SMD_3216m | Top | 8.4843 | 4.8425 | 180
C109 | C_Cap_Cera_SMD_3216m | Top | 8.4961 | 3.5039 | 90
C3 | C_Cap_Pol_SMD_3528m | Top | 3.0551 | 5.1378 | 90
C17 | C_Cap_Pol_SMD_3528m | Top | 2.0787 | 3.6496 | 180
C25 | C_Cap_Pol_SMD_3528m | Top | 2.5748 | 2.7205 | 0
C27 | C_Cap_Pol_SMD_3528m | Top | 3.4016 | 2.4884 | 270
C37 | C_Cap_Pol_SMD_3528m | Top | 3.0551 | 5.4016 | 270
C81 | C_Cap_Pol_SMD_3528m | Top | 2.937 | 4.437 | 180
C82 | C_Cap_Pol_SMD_3528m | Top | 2.6614 | 4.437 | 180
C125 | C_Cap_Pol_SMD_3528m | Top | 3.0591 | 2.7205 | 0
J14 | C_Con2_2-54_solder_wire | Top | 5.0512 | 1.811 | 270
J16 | C_Con2_2-54_solder_wire | Top | 5.9291 | 4.3189 | 0
J7 | C_Con4_FAN_2-54 | Top | 0.2795 | 2.2087 | 0
J18 | C_Con8_SPI_Ext_Ada3328_RTD | Top | 1.2058 | 0.7718 | 90
J8 | C_Con9_IC2_Ext_Adafruit | Top | 1.6782 | 0.8218 | 90
J17 | C_Con9_SPI_Ext_Ada3263_TC_AMP | Top | 1.4578 | 0.8218 | 90
VR5 | C_DCDC_1ch_7pin_2-54pitch | Top | 2.5 | 5.2784 | 0
VR4 | C_DCDC_2ch_7pin_2-54pitch | Top | 2.5 | 4.7508 | 0
L4 | C_Ferride_Bead_SMD_3216m | Top | 8.5157 | 0.752 | 180
L5 | C_Ferride_Bead_SMD_3216m | Top | 8.5157 | 0.5551 | 180
RS1 | C_FR4-2321-4pin_+TO220+HeatSink | Top | 7.5591 | 3.1024 | 0
FS4 | C_Fuse_6-3x32mm_&_5x20mm | Top | 8.1378 | 4.7419 | 90
FS1 | C_Fuse_22-6 | Top | 1.0118 | 4.8228 | 0
L6 | C_IND_SMD_4-8_4-8_SQRpad | Top | 1.4094 | 5.3583 | 0
L7 | C_IND_SMD_4-8_4-8_SQRpad | Top | 3.315 | 5.374 | 0
L8 | C_IND_SMD_4-8_4-8_SQRpad | Top | 2.6417 | 4.1811 | 270
L9 | C_IND_SMD_4-8_4-8_SQRpad | Top | 3.0354 | 4.1811 | 270
T4 | C_IRFB4227+MUR1520_+Heatsink | Top | 7.0709 | 4.0492 | 180
J2 | C_Jump10_2-54 | Top | 0.7795 | 3.1417 | 90
T1 | C_MosFET+RA-T2X-xxE_HeatSink | Top | 6.9528 | 4.9724 | 180
NTC1 | C_NTC_SMD_2012m | Top | 4.8425 | 1.8189 | 90
SW1 | C_Relay_DPDT_1C-Latch | Top | 5.7563 | 1.2126 | 180
SW2 | C_Relay_DPDT_1C-Latch | Top | 0.5791 | 1.7717 | 180
SW3 | C_Relay_DPDT_1C-Latch | Top | 6.9055 | 0.9217 | 270
SW4 | C_Relay_DPDT_1C-Latch | Top | 6.8697 | 0.3583 | 0
R1 | C_RES_SMD_2012m | Top | 1.0079 | 2.8898 | 0
R2 | C_RES_SMD_2012m | Top | 1.0079 | 2.9921 | 0
R3 | C_RES_SMD_2012m | Top | 1.0079 | 3.0945 | 0
R4 | C_RES_SMD_2012m | Top | 1.0079 | 3.1969 | 0
R5 | C_RES_SMD_2012m | Top | 1.0079 | 3.2992 | 0
R7 | C_RES_SMD_2012m | Top | 1.748 | 4.1299 | 180
R8 | C_RES_SMD_2012m | Top | 1.748 | 4.0197 | 180
R9 | C_RES_SMD_2012m | Top | 1.6535 | 3.2874 | 90
R10 | C_RES_SMD_2012m | Top | 2.0394 | 2.4606 | 0
R11 | C_RES_SMD_2012m | Top | 2.5984 | 1.8543 | 0
R12 | C_RES_SMD_2012m | Top | 2.0394 | 2.3504 | 0
R13 | C_RES_SMD_2012m | Top | 1.9134 | 2.248 | 0
R14 | C_RES_SMD_2012m | Top | 1.9134 | 2.1496 | 0
R15 | C_RES_SMD_2012m | Top | 7.2165 | 0.7047 | 180
R16 | C_RES_SMD_2012m | Top | 7.2165 | 0.5866 | 180
R17 | C_RES_SMD_2012m | Top | 7.2165 | 0.8465 | 180
R21 | C_RES_SMD_2012m | Top | 6.5827 | 3.689 | 0
R22 | C_RES_SMD_2012m | Top | 7.2165 | 0.9449 | 180
R23 | C_RES_SMD_2012m | Top | 4.3189 | 0.8661 | 0
R24 | C_RES_SMD_2012m | Top | 4.622 | 2.7441 | 270
R25 | C_RES_SMD_2012m | Top | 4.7165 | 2.7441 | 270
R26 | C_RES_SMD_2012m | Top | 4.5276 | 2.7441 | 270
R27 | C_RES_SMD_2012m | Top | 6 | 1.6378 | 180
R28 | C_RES_SMD_2012m | Top | 6 | 1.7362 | 180
R29 | C_RES_SMD_2012m | Top | 5.0551 | 3.4134 | 0
R30 | C_RES_SMD_2012m | Top | 5.0551 | 2.9409 | 0
R31 | C_RES_SMD_2012m | Top | 5.0551 | 3.0354 | 0
R32 | C_RES_SMD_2012m | Top | 6.8465 | 2.1535 | 180
R33 | C_RES_SMD_2012m | Top | 6.8465 | 2.2559 | 180
R34 | C_RES_SMD_2012m | Top | 6.8465 | 1.8661 | 180
R35 | C_RES_SMD_2012m | Top | 6.8465 | 1.9685 | 180
R36 | C_RES_SMD_2012m | Top | 6.8465 | 1.5118 | 180
R37 | C_RES_SMD_2012m | Top | 6.8465 | 1.6142 | 180
R38 | C_RES_SMD_2012m | Top | 6.5197 | 3 | 0
R39 | C_RES_SMD_2012m | Top | 6.5197 | 2.9016 | 0
R40 | C_RES_SMD_2012m | Top | 6.5197 | 2.6142 | 0
R41 | C_RES_SMD_2012m | Top | 6.5197 | 2.5079 | 0
R42 | C_RES_SMD_2012m | Top | 1.5591 | 4.0197 | 180
R43 | C_RES_SMD_2012m | Top | 1.8661 | 3.0669 | 270
R46 | C_RES_SMD_2012m | Top | 5.5827 | 3.4606 | 90
R47 | C_RES_SMD_2012m | Top | 5.6614 | 3.6024 | 180
R48 | C_RES_SMD_2012m | Top | 6.1102 | 3.2559 | 180
R49 | C_RES_SMD_2012m | Top | 6.1496 | 3.4055 | 90
R50 | C_RES_SMD_2012m | Top | 5.7087 | 2.9764 | 180
R51 | C_RES_SMD_2012m | Top | 6.3031 | 3.4055 | 0
R52 | C_RES_SMD_2012m | Top | 6.3031 | 3.2165 | 180
R53 | C_RES_SMD_2012m | Top | 5.7087 | 2.874 | 0
R54 | C_RES_SMD_2012m | Top | 5.6772 | 2.7756 | 0
R55 | C_RES_SMD_2012m | Top | 5.0551 | 3.1299 | 0
R56 | C_RES_SMD_2012m | Top | 5.0551 | 3.2244 | 0
R57 | C_RES_SMD_2012m | Top | 5.0551 | 3.3189 | 0
R58 | C_RES_SMD_2012m | Top | 5.7835 | 1.4724 | 270
R59 | C_RES_SMD_2012m | Top | 5.6457 | 1.437 | 180
R60 | C_RES_SMD_2012m | Top | 5.811 | 0.874 | 180
R61 | C_RES_SMD_2012m | Top | 5.811 | 0.9724 | 180
R62 | C_RES_SMD_2012m | Top | 4.9055 | 2.7441 | 270
R63 | C_RES_SMD_2012m | Top | 4.811 | 2.7441 | 270
R64 | C_RES_SMD_2012m | Top | 2.1417 | 3.2244 | 90
R65 | C_RES_SMD_2012m | Top | 2.0315 | 3.2244 | 90
R66 | C_RES_SMD_2012m | Top | 5.0551 | 2.7165 | 0
R67 | C_RES_SMD_2012m | Top | 5.0551 | 2.815 | 0
R68 | C_RES_SMD_2012m | Top | 0.4724 | 3.9764 | 270
R69 | C_RES_SMD_2012m | Top | 0.5512 | 4.3012 | 180
R70 | C_RES_SMD_2012m | Top | 1.7717 | 3.0669 | 90
R71 | C_RES_SMD_2012m | Top | 0.874 | 2.7717 | 180
R72 | C_RES_SMD_2012m | Top | 0.874 | 2.6732 | 0
R73 | C_RES_SMD_2012m | Top | 0.874 | 2.5748 | 180
R74 | C_RES_SMD_2012m | Top | 2.5984 | 1.9488 | 0
R75 | C_RES_SMD_2012m | Top | 2.315 | 1.2441 | 180
R76 | C_RES_SMD_2012m | Top | 2.315 | 1.3465 | 180
R77 | C_RES_SMD_2012m | Top | 2.315 | 1.4449 | 180
R78 | C_RES_SMD_2012m | Top | 3.2835 | 1.7362 | 90
R79 | C_RES_SMD_2012m | Top | 3.4606 | 0.2717 | 180
R80 | C_RES_SMD_2012m | Top | 3.7677 | 0.3268 | 180
R81 | C_RES_SMD_2012m | Top | 3.8543 | 0.9094 | 180
R82 | C_RES_SMD_2012m | Top | 3.5039 | 0.9488 | 180
R83 | C_RES_SMD_2012m | Top | 3.315 | 0.8465 | 180
R84 | C_RES_SMD_2012m | Top | 3.2638 | 0.374 | 180
R85 | C_RES_SMD_2012m | Top | 4.1339 | 1.1063 | 180
R86 | C_RES_SMD_2012m | Top | 4.2717 | 1.1378 | 270
R87 | C_RES_SMD_2012m | Top | 4.6929 | 0.9409 | 180
R88 | C_RES_SMD_2012m | Top | 8.1142 | 2.3622 | 180
R90 | C_RES_SMD_2012m | Top | 4.4331 | 2.7441 | 270
R91 | C_RES_SMD_2012m | Top | 3.626 | 4.7087 | 90
R92 | C_RES_SMD_2012m | Top | 6.0433 | 0.4016 | 270
R93 | C_RES_SMD_2012m | Top | 0.9331 | 1.7992 | 0
R95 | C_RES_SMD_2012m | Top | 3.3228 | 4.0433 | 0
R96 | C_RES_SMD_2012m | Top | 1.689 | 4.3346 | 180
R97 | C_RES_SMD_2012m | Top | 3.7362 | 3.7874 | 180
R98 | C_RES_SMD_2012m | Top | 4.0866 | 4.3504 | 180
R99 | C_RES_SMD_2012m | Top | 3.8386 | 4.3386 | 0
R100 | C_RES_SMD_2012m | Top | 4.0354 | 4.1811 | 90
R101 | C_RES_SMD_2012m | Top | 3.8386 | 4.4331 | 180
R102 | C_RES_SMD_2012m | Top | 4.3465 | 5.2992 | 0
R103 | C_RES_SMD_2012m | Top | 4.1772 | 4.1811 | 270
R104 | C_RES_SMD_2012m | Top | 4.5512 | 5.1378 | 90
R105 | C_RES_SMD_2012m | Top | 4.2992 | 4.6339 | 0
R106 | C_RES_SMD_2012m | Top | 4.1654 | 4.8543 | 270
R107 | C_RES_SMD_2012m | Top | 4.4882 | 4.7362 | 0
R108 | C_RES_SMD_2012m | Top | 5.0394 | 4.8543 | 270
R109 | C_RES_SMD_2012m | Top | 5.3858 | 4.7362 | 0
R110 | C_RES_SMD_2012m | Top | 4.8976 | 4.9213 | 270
R111 | C_RES_SMD_2012m | Top | 4.8031 | 4.9213 | 270
R112 | C_RES_SMD_2012m | Top | 3.4016 | 1.5984 | 180
R113 | C_RES_SMD_2012m | Top | 5.4843 | 5.0787 | 0
R114 | C_RES_SMD_2012m | Top | 5.1732 | 5.2953 | 180
R115 | C_RES_SMD_2012m | Top | 5.9252 | 4.6969 | 90
R116 | C_RES_SMD_2012m | Top | 5.9094 | 5.2087 | 0
R117 | C_RES_SMD_2012m | Top | 2.0827 | 3.4173 | 0
R118 | C_RES_SMD_2012m | Top | 4.5039 | 2.0157 | 180
R119 | C_RES_SMD_2012m | Top | 4.5039 | 2.1142 | 180
R120 | C_RES_SMD_2012m | Top | 4.7874 | 1.6496 | 0
R121 | C_RES_SMD_2012m | Top | 4.9764 | 2.3504 | 0
R122 | C_RES_SMD_2012m | Top | 4.6693 | 1.8543 | 0
R123 | C_RES_SMD_2012m | Top | 4.7795 | 2.3386 | 0
R124 | C_RES_SMD_2012m | Top | 1.9016 | 1.0315 | 0
R125 | C_RES_SMD_2012m | Top | 1.5591 | 2.0512 | 90
R126 | C_RES_SMD_2012m | Top | 1.6535 | 2.0512 | 90
R127 | C_RES_SMD_2012m | Top | 1.6063 | 1.4685 | 90
R128 | C_RES_SMD_2012m | Top | 1.9016 | 1.1339 | 0
R129 | C_RES_SMD_2012m | Top | 1.5591 | 4.1969 | 180
R130 | C_RES_SMD_2012m | Top | 0.9331 | 1.6811 | 0
R131 | C_RES_SMD_2012m | Top | 0.9921 | 2.2835 | 0
R132 | C_RES_SMD_2012m | Top | 0.9921 | 2.0945 | 0
R133 | C_RES_SMD_2012m | Top | 0.9921 | 2.189 | 0
R134 | C_RES_SMD_2012m | Top | 0.9921 | 2 | 0
R135 | C_RES_SMD_2012m | Top | 4.3465 | 4.4134 | 90
R136 | C_RES_SMD_2012m | Top | 4.4449 | 4.4134 | 90
R137 | C_RES_SMD_2012m | Top | 4.5433 | 4.4134 | 90
R138 | C_RES_SMD_2012m | Top | 4.6417 | 4.4134 | 90
R139 | C_RES_SMD_2012m | Top | 1.9016 | 0.9291 | 0
R140 | C_RES_SMD_2012m | Top | 1.9016 | 0.8268 | 0
R141 | C_RES_SMD_2012m | Top | 4.5906 | 3.5079 | 90
R142 | C_RES_SMD_2012m | Top | 4.4961 | 3.5079 | 90
R143 | C_RES_SMD_2012m | Top | 4.7795 | 3.5079 | 90
R144 | C_RES_SMD_2012m | Top | 4.685 | 3.5079 | 90
R154 | C_RES_SMD_2012m | Top | 3.378 | 1.7362 | 90
R155 | C_RES_SMD_2012m | Top | 3.2126 | 3.5827 | 90
R156 | C_RES_SMD_2012m | Top | 4.9921 | 5.2953 | 0
R157 | C_RES_SMD_2012m | Top | 2.2874 | 2.9055 | 90
R158 | C_RES_SMD_2012m | Top | 5.9685 | 5.0551 | 90
R159 | C_RES_SMD_2012m | Top | 1.9528 | 0.7244 | 0
R160 | C_RES_SMD_2012m | Top | 1.9528 | 0.622 | 0
R161 | C_RES_SMD_2012m | Top | 4.2756 | 2.7835 | 0
R162 | C_RES_SMD_2012m | Top | 4.2756 | 2.6811 | 0
R163 | C_RES_SMD_2012m | Top | 4.1614 | 3.0354 | 0
R164 | C_RES_SMD_2012m | Top | 4.1614 | 3.1339 | 0
R165 | C_RES_SMD_2012m | Top | 6.5551 | 1.1654 | 0
R166 | C_RES_SMD_2012m | Top | 6.5551 | 1.0551 | 0
R167 | C_RES_SMD_2012m | Top | 6.5551 | 0.8268 | 0
R168 | C_RES_SMD_2012m | Top | 6.5551 | 0.7165 | 0
R169 | C_RES_SMD_2012m | Top | 4.0394 | 4.8189 | 180
R170 | C_RES_SMD_2012m | Top | 4.9016 | 4.7441 | 0
R171 | C_RES_SMD_2012m | Top | 5.311 | 5.3228 | 270
R6 | C_RES_SMD_3216m | Top | 1.9449 | 4.5512 | 270
R18 | C_RES_SMD_3216m | Top | 7.3307 | 0.3189 | 270
R19 | C_RES_SMD_3216m | Top | 6.5 | 0.3465 | 180
R20 | C_RES_SMD_3216m | Top | 6.5 | 0.4764 | 180
R44 | C_RES_SMD_3216m | Top | 2.6417 | 3.9173 | 270
R45 | C_RES_SMD_3216m | Top | 3.0354 | 3.9173 | 270
R89 | C_RES_SMD_3216m | Top | 8.2953 | 0.752 | 0
R94 | C_RES_SMD_3216m | Top | 3.3661 | 4.248 | 90
R145 | C_RES_SMD_3216m | Top | 1.7008 | 5.3031 | 0
R146 | C_RES_SMD_3216m | Top | 1.7008 | 5.4213 | 0
R147 | C_RES_SMD_3216m | Top | 3.2362 | 5.126 | 270
R148 | C_RES_SMD_3216m | Top | 3.3543 | 5.126 | 270
R149 | C_RES_SMD_3216m | Top | 8.3858 | 0.9646 | 180
R150 | C_RES_SMD_3216m | Top | 8.0197 | 0.7598 | 270
R151 | C_RES_SMD_3216m | Top | 7.8268 | 0.7598 | 270
R152 | C_RES_SMD_3216m | Top | 7.6378 | 0.7598 | 90
R153 | C_RES_SMD_3216m | Top | 7.4488 | 0.7598 | 270
R172 | C_RES_SMD_3216m | Top | 6.5 | 0.2362 | 180
R173 | C_RES_SMD_3216m | Top | 6.5 | 0.5866 | 180
R174 | C_RES_SMD_3216m | Top | 8.4724 | 4.4685 | 0
R175 | C_RES_SMD_3216m | Top | 8.4843 | 5.0079 | 0
R176 | C_RES_SMD_3216m | Top | 8.4961 | 3.7323 | 90
RS5 | C_RES_SMD_3216m | Top | 7.937 | 1.9291 | 180
RS6 | C_RES_SMD_3216m | Top | 7.937 | 1.5433 | 180
RS2 | C_RES_SMD_6432m | Top | 7.937 | 1.7756 | 0
RS3 | C_RES_SMD_6432m | Top | 7.937 | 1.3858 | 0
RS4 | C_RES_SMD_6432m | Top | 7.937 | 2.1732 | 0
C1 | C_SMD_CAP_POL_6.6 | Top | 2.9488 | 3.5315 | 180
C2 | C_SMD_CAP_POL_6.6 | Top | 2.5394 | 3.5315 | 0
C4 | C_SMD_CAP_POL_6.6 | Top | 1.0866 | 5.2874 | 90
C79 | C_SMD_CAP_POL_8.3 | Top | 3.2677 | 4.7283 | 90
C78 | C_SMD_CAP_POL_10.3 | Top | 1.7874 | 4.9252 | 90
TP6 | C_Test_Point_1 | Top | 1.6339 | 2.2126 | 0
TP7 | C_Test_Point_1 | Top | 5.378 | 1.6339 | 0
TP8 | C_Test_Point_1 | Top | 5.4134 | 0.3268 | 0
TP9 | C_Test_Point_1 | Top | 4.4882 | 1.6417 | 0
TP10 | C_Test_Point_1 | Top | 4.6181 | 2.4488 | 0
TP11 | C_Test_Point_1 | Top | 4.9055 | 1.063 | 0
TP12 | C_Test_Point_1 | Top | 2.9803 | 1.0118 | 0
TP13 | C_Test_Point_1 | Top | 2.9291 | 0.4449 | 0
TP14 | C_Test_Point_1 | Top | 3.3504 | 2.3031 | 0
TP16 | C_Test_Point_1 | Top | 3.4606 | 3.8189 | 0
TP17 | C_Test_Point_1 | Top | 3.2795 | 2.1969 | 0
TP18 | C_Test_Point_1 | Top | 4.6417 | 5 | 0
TP19 | C_Test_Point_1 | Top | 4.2165 | 4.4528 | 0
TP20 | C_Test_Point_1 | Top | 5.1102 | 4.4606 | 0
TP21 | C_Test_Point_1 | Top | 5.1575 | 5.4094 | 0
TP22 | C_Test_Point_1 | Top | 4.1614 | 4.0709 | 0
TP23 | C_Test_Point_1 | Top | 3.7953 | 4.5039 | 0
TP24 | C_Test_Point_1 | Top | 1.7677 | 2.1102 | 0
TP25 | C_Test_Point_1 | Top | 2.1063 | 2.2598 | 0
TP26 | C_Test_Point_1 | Top | 1.9331 | 2.4606 | 0
TP27 | C_Test_Point_1 | Top | 2.0315 | 3.063 | 0
TP28 | C_Test_Point_1 | Top | 2.1772 | 3.0945 | 0
TP29 | C_Test_Point_1 | Top | 1.8228 | 3.3228 | 0
TP30 | C_Test_Point_1 | Top | 1.8071 | 2.9094 | 0
TP31 | C_Test_Point_1 | Top | 1.6772 | 3.752 | 0
TP1 | C_Test_Point_2 | Top | 1.8701 | 3.7244 | 90
TP2 | C_Test_Point_2 | Top | 2.4921 | 3.2441 | 180
TP3 | C_Test_Point_2 | Top | 3.3504 | 3.2953 | 0
TP4 | C_Test_Point_2 | Top | 2.5866 | 2.4409 | 180
TP5 | C_Test_Point_2 | Top | 3.2677 | 2.811 | 90
TP15 | C_Test_Point_2 | Top | 5.9016 | 5.3425 | 180
TP32 | C_Test_Point_2 | Top | 3.9055 | 5.4331 | 90
TP33 | C_Test_Point_2 | Top | 1.8583 | 5.3346 | 90
RT1 | C_Trim_SMD_Burns_TopAdj | Top | 5.4724 | 5.2874 | 180
RT2 | C_Trim_SMD_Burns_TopAdj | Top | 4.0551 | 4.6654 | 90
RT3 | C_Trim_SMD_Burns_TopAdj | Top | 4.9528 | 4.5866 | 90
VR2 | C_Volt_Reg_POS_TO220_+Small_HS | Top | 2.1835 | 4.1132 | 180
U3 | DAC8550IBDGKT_16bit DAC | Top | 2.8425 | 2.0827 | 90
U17 | DG408LEDY_8-1_MUX | Top | 2.9213 | 1.2756 | 0
U9 | DG409DY-T1-E3 | Top | 6.2362 | 2.0118 | 270
U2 | ISO3088DW | Top | 1.1969 | 4.0551 | 90
U10 | IX4427_2-CH_M-FET_DRV | Top | 6.252 | 2.9764 | 270
U11 | IX4427_2-CH_M-FET_DRV | Top | 6.252 | 2.5827 | 270
U4 | MAX1163_16bit_ADC | Top | 2.8425 | 1.8228 | 90
U26 | MAX4659_A_switch_SPDT | Top | 5.7913 | 4.9724 | 180
U27 | MCP1501_Vref | Top | 4.2717 | 2.1024 | 0
U14 | MP6513GJ-P_H-bridge | Top | 5.6024 | 0.9488 | 180
U15 | MP6513GJ-P_H-bridge | Top | 0.7953 | 2.1417 | 90
U31 | MP6513GJ-P_H-bridge | Top | 6.252 | 0.9685 | 180
U32 | MP6513GJ-P_H-bridge | Top | 6.252 | 0.7165 | 180
U21 | MUX508IDR | Top | 4.6063 | 4.0984 | 180
U30 | MUX508IDR | Top | 5.4921 | 4.0984 | 180
U18 | OP1177_singl_op-amp | Top | 3.2717 | 1.311 | 0
U20 | OP1177_singl_op-amp | Top | 4.6929 | 1.122 | 270
U12 | OP2177_dual_op-amp | Top | 5.811 | 3.3819 | 270
U19 | OP2177_dual_op-amp | Top | 3.3386 | 0.6102 | 180
U23 | OP2177_dual_op-amp | Top | 3.8543 | 4.0157 | 0
U24 | OP2177_dual_op-amp | Top | 4.3661 | 4.9724 | 0
U25 | OP2177_dual_op-amp | Top | 5.2598 | 4.9724 | 0
U28 | OP2177_dual_op-amp | Top | 4.7677 | 2.1024 | 0
U16 | PCA9555_IO_EXP | Top | 4.5984 | 3.122 | 0
U5 | REF198FSZ | Top | 3.0394 | 2.449 | 270
D3 | SM_Diode_2_Ser_SOD23 | Top | 6.2874 | 0.3031 | 270
D4 | SM_Diode_2_Ser_SOD23 | Top | 6.2874 | 0.5 | 90
D18 | SM_Diode_2_Ser_SOD23 | Top | 3.7677 | 0.7283 | 270
D19 | SM_Diode_2_Ser_SOD23 | Top | 3.7244 | 0.4764 | 90
D20 | SM_Diode_2_Ser_SOD23 | Top | 3.1142 | 0.8937 | 90
D21 | SM_Diode_2_Ser_SOD23 | Top | 3.063 | 0.3268 | 270
D33 | SM_Diode_2_Ser_SOD23 | Top | 3.3228 | 3.9173 | 180
D2 | SM_Diode_DO214AA | Top | 0.6378 | 5.311 | 270
D31 | SM_Diode_DO214AA | Top | 3.6535 | 5.1024 | 180
D32 | SM_Diode_DO214AA | Top | 3.6535 | 4.9094 | 180
D12 | SM_Diode_SOD323 | Top | 5.937 | 2.185 | 0
D13 | SM_Diode_SOD323 | Top | 6.563 | 2.1417 | 90
D17 | SM_Diode_SOD323 | Top | 3.2362 | 1.9134 | 90
D24 | SM_Diode_SOD323 | Top | 5.1969 | 4.6339 | 180
D25 | SM_Diode_SOD323 | Top | 5.937 | 0.685 | 270
D26 | SM_Diode_SOD323 | Top | 0.6417 | 2.3819 | 90
D27 | SM_Diode_SOD323 | Top | 2.9291 | 3.9173 | 270
D28 | SM_Diode_SOD323 | Top | 2.748 | 3.9173 | 90
D34 | SM_Diode_SOD323 | Top | 2.811 | 2.6693 | 90
D36 | SM_Diode_SOD323 | Top | 2.5906 | 2.5591 | 180
D38 | SM_Diode_SOD323 | Top | 1.0551 | 1.4488 | 180
LED1 | SM_LED_0805i_2012m | Top | 0.2913 | 2.8346 | 270
LED2 | SM_LED_0805i_2012m | Top | 0.2913 | 2.6535 | 270
LED3 | SM_LED_0805i_2012m | Top | 0.2913 | 2.4724 | 270
T9 | SM_MosFET_P-ch_SOT23-3 | Top | 0.6732 | 3.7402 | 0
T2 | SM_MosFET_SOIC8_E4 | Top | 7.3465 | 1.8031 | 90
T3 | SM_MosFET_SOIC8_E4 | Top | 7.3465 | 1.4094 | 90
T7 | SM_MosFET_SOIC8_E4 | Top | 7.3465 | 2.1969 | 90
D1 | SM_Zehner_Diode_DO214 | Top | 0.8189 | 5.311 | 270
D10 | SM_Zehner_Diode_SOD106 | Top | 7.2047 | 0.3583 | 270
D16 | SM_Zehner_Diode_SOD106 | Top | 7.0709 | 3.689 | 180
D5 | SM_Zehner_Diode_SOD123 | Top | 5.2598 | 0.2717 | 180
D6 | SM_Zehner_Diode_SOD123 | Top | 5.4449 | 0.6181 | 90
D7 | SM_Zehner_Diode_SOD123 | Top | 5.7717 | 0.7087 | 180
D8 | SM_Zehner_Diode_SOD123 | Top | 0.6417 | 2.1575 | 270
D22 | SM_Zehner_Diode_SOD123 | Top | 2.8898 | 2.9291 | 270
D23 | SM_Zehner_Diode_SOD123 | Top | 2.5354 | 2.9291 | 90
D29 | SM_Zehner_Diode_SOD123 | Top | 2.9724 | 3.752 | 0
D30 | SM_Zehner_Diode_SOD123 | Top | 2.7047 | 3.752 | 0
D35 | SM_Zehner_Diode_SOD123 | Top | 0.8937 | 3.748 | 0
D37 | SM_Zehner_Diode_SOD123 | Top | 1.0512 | 1.3543 | 180
U13 | SN74LVC1G175DBVT-FlipFlop | Top | 5.5039 | 2.9134 | 180
T5 | SOT32_MosFET_N-ch | Top | 6.4882 | 3.2913 | 90
T6 | SOT32_MosFET_N-ch | Top | 5.9134 | 2.9213 | 270
VR3 | Volt_Reg_Neg_SOIC | Top | 3.0709 | 3.0984 | 0
VR1 | Volt_Reg_Pos_SOIC | Top | 2.7126 | 3.0984 | 0
XTAL1 | XTAL_3.2_2.5m | Top | 2 | 2.7441 | 90

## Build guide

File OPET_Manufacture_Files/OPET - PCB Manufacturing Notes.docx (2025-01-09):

OPET

Open PV Electrical Tool

PCB manufacturing Notes

OPET REV 1.4

Contact Byron McDanold (NREL) in case of questions:

May 2, 2023

Version 0.93 first draft

byron.mcdanold@nrel.gov 303-275-4706

# 1 Introduction

- This document contains further information with regards to the PCB design and PCB manufacturing of OPET boards
- OPENT comes in 2 versions: low-current (340 mA) and high-current (15 A) version
  - Both use the same PCB with some changes in components
- Includes:
  - PCB manufacturing requirements
  - PCB assembly requirements and instructions

## 1.1 Overview Low-Current OPET version

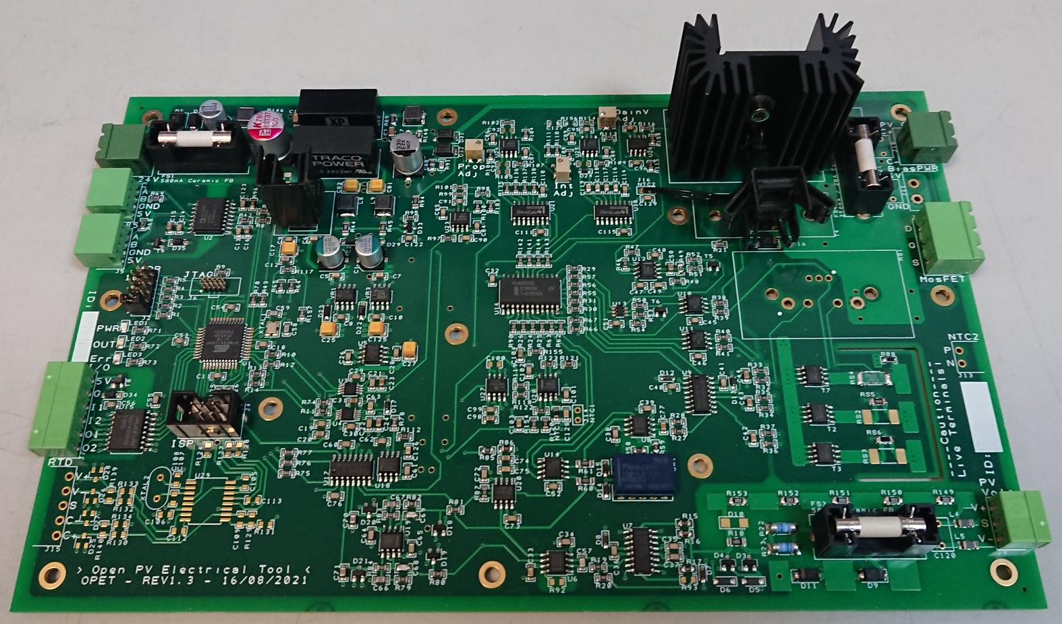
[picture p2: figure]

Figure 1: Photo of previous test version of low-current OPET, the current version is slightly different

## 1.2 Overview High-Current OPET version

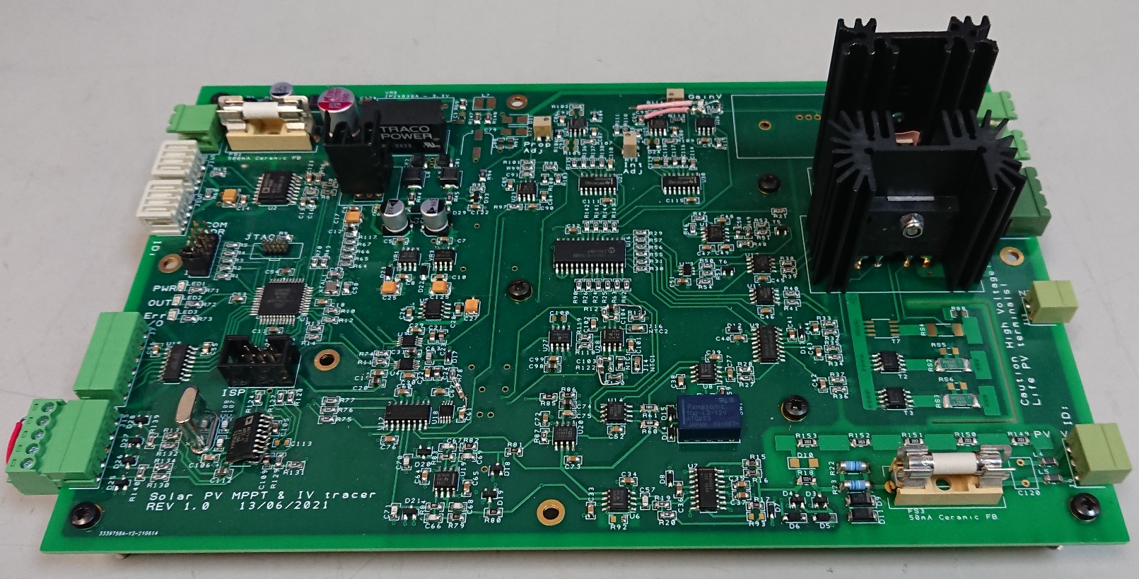
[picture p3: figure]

Figure 2: Photo of previous test version of high-current OPET, the current version is slightly different

# 2 PCB manufacturing requirements

- The OPET board is a 4-layer PCB
- Following copper layer thickness is recommended:
  - top and bottom layer 1 and 4
    - 1oz copper thickness (~35 µm)
  - inner layers 2 and 3:
    - 2oz copper thickness (~70 µm)
- following 4-layer PCB structure should be used (see Figure 1):
  - the full PCB should be 1.6mm thick
  - the layers 1 to 2 and 3 to 4 should be separated with a thin prepreg sheet (~0.2 mm)
  - the layer stack should have a centre core sublayer (~1.0 mm) between the inner layers 2 & 3
    - high voltage parts of the OPET PCB are separated such that the inner core sublayer is the main insulator where tracks with high voltage potential cross

Figure 3: recommended PCB layer stack configuration, use 2oz of copper thickness for inner layers and 1oz of copper thickness for outer layers

- PCB material:
  - FR4 TG155 or similar
      - good high temperature resistance is needed
- PCB finish:
  - should be ENIG (Electroless Nickel Immersion Gold)

# 3 PCB Assembly requirements and instructions

## 3.1 Component orientation

- Before PCB assembly correct orientation of components on the PCB should be checked
  - orientation has to be correct for assembly with a pick and place machine to be successful
  - a component placement preview image/diagram from the manufacturer should help make sure orientation is correct before assembly starts
- following sections detail the zero-orientation various component package types

### 3.1.1 Orientation definitions

- Zero rotation as shown in the figures
- 2 pin diodes:
  - pin 1, left: C – Cathode
  - pin 2, right: A – Anode
  - zero rotation has pin 1 on left side

Figure 4: 2-pin diode, zero rotation, pin 1 shown on the left side

- 2 pin polarized capacitor:
  - pin 1, left: -, negative
  - pin 2, right: +, positive
  - zero rotation has pin 1 on left side

Figure 5: 2-pin polarized capacitor, zero rotation, pin 1 shown on the left side

- 2 pin electrolytic capacitor:
  - pin 1, left: -, negative
  - pin 2, right: +, positive, also marked with the (+) sign
  - zero rotation has pin 1 on left side

Figure 6: 2-pin polarized electrolytic capacitor, zero rotation, pin 1 shown on the left side

- 44-lead TQFP:
  - Pin 1 marked with extended line on silkscreen
  - Zero rotation has pin 1 in lower left corner

Figure 7: 44-lead TQFP, zero rotation, extended line on pin 1 shown in the lower left corner

- SOIC, µMax, TSSOP and similar ICs:
  - Pin 1 marked with extended line on silkscreen
  - Zero rotation has pin 1 in lower left corner

Figure 8: SOIC, µMax, TSSOP and similar ICs, zero rotation, extended line on pin 1 shown in the lower left corner

- SOT (the exception):
  - Pin 1 marked with extended line on silkscreen
  - Zero rotation has pin 1 in lower right corner

Figure 9: SOP, zero rotation, extended line on pin 1 shown in the lower right corner

- Relays, DIL, DIP:
  - Pin 1 marked with notch in line on silkscreen
  - Zero rotation has pin 1 in lower left corner

Figure 10: Relays, DIL, DIP, zero rotation, notch marking near pin 1 shown in the lower right corner

- Through-hole SIL Connectors:
  - Connector cable input direction / plug entry on open side of silkscreen shape
  - Zero rotation has pin 1 on the left side and open side of silkscreen on the bottom

Figure 11: Through-hole SIL Connectors, zero rotation, cable input direction / plug entry from the open shape side, pin 1 on left side

- SIL components, SIL headers:
  - Pin 1 marked with dot
  - Zero rotation has pin 1 and dot marking on the left side

Figure 12: SIL components and headers, zero rotation, pin 1 on left side marked with dot

- Through-hole header connectors:
  - Pin 1 marked with dot
  - Zero rotation has pin 1 and dot marking on the lower left side, notch marking pointing towards the bottom

Figure 13: Through-hole header connectors, zero rotation, pin 1 on lower left corner marked with dot and notch marking pointing towards the bottom

## 3.2 Through-hole components with heatsinks

- Components with heatsinks have multiple parts on the same component identifier with an additional letter at the end (for example VR2_A for the voltage regulator and VR2_B for the heat sink)
- This section details how to mount components with heatsinks onto the OPET board and where insulating pad or thermal paste is needed
- some instructions differ between high and low current OPET versions
- When soldering through hole components with large heatsinks to the PCB:
  - make sure there is a ~1.5 mm gap between the heatsink/component body and PCB
  - This is to make sure that the heatsink is not contacting and shorting tracks on the PCB and to maintain voltage rating
  - solder the heatsink locating pins to the PCB to stop the component from moving or vibrating
- When instructed to use a TO-220 electrical insulating pad:
  - The part then needs to be mounted with an electrically isolating but thermally bonding pad and nylon bush
  - a TO-220 insulating kit such as Newark 50P9593 (MK3306) should work
  - Use a thin pad with high thermal conductivity
  - Max voltage to insulate is 150 V under normal operating conditions
  - The nylon bush is needed to make sure the screw does not make a new contact
  - Make sure the nylon bush has a deep enough rim to go through the component mounting hole and partly into the heatsink screw hole
    - A nylon bush rim that is too shallow will cause a short between component and heatsink
  - Use metal washers at screw head and nut end to spread the contact force on the nylon bush

### 3.2.1 All OPET versions

- VR2:
  - the 5V regulator should be mounted onto the heatsink without any electrically insulating pads or thermal paste
  - bend the heatsink fins as needed to secure the TO-220 voltage regulator
  - If a hole for screw mounting is available, secure part using M3 screw, nut and washers

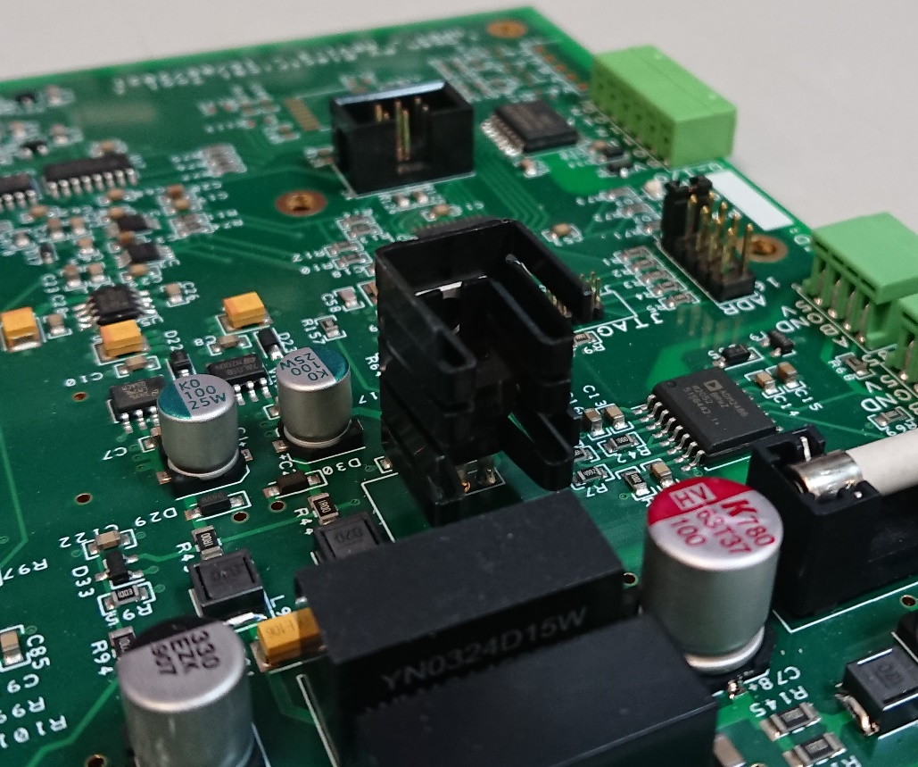
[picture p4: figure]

Figure 14: Image of VR2 on OPET PCB, the actual heatsink may vary slight and will be either clamp-fit or screw-fit

### 3.2.2 Low-Current OPET version

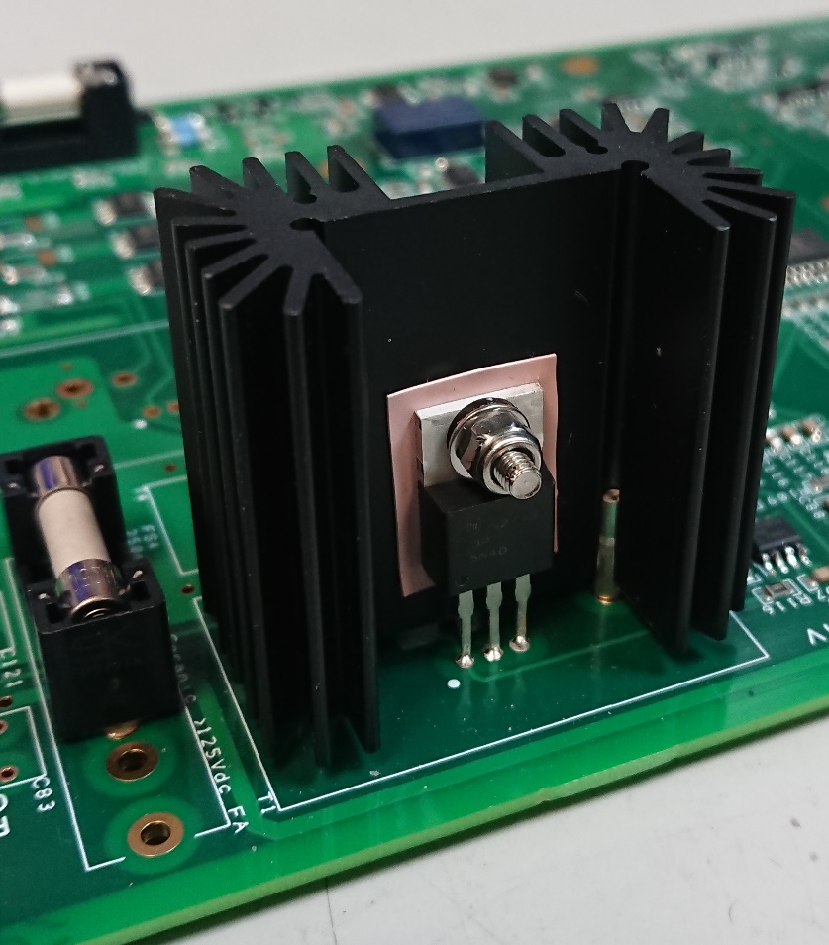
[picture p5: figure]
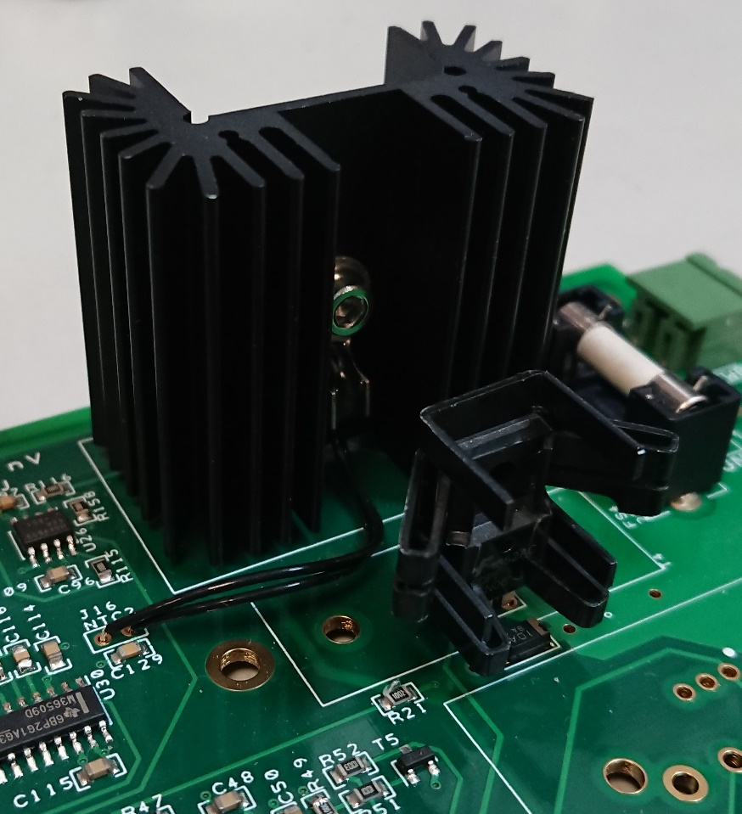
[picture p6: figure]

Figure 14: Low-current OPET: Left: front side of T1 with driver MosFET; Right: rear side of T1 with NTC sensor bolted to the back of heatsink and T4 MosFET fixed to small heatsink using either clamp-fit or screw-fit as required

- T1:
  - The driver MosFET needs to be mounted with insulating pad and bush
  - In addition, the NTC sensor needs to be mounted to the heatsink
  - The NTC sensor should be mounted at the back of the heatsink, on the opposite side of the MosFET
  - The NTC leads need to be wire soldered onto J16
  - Solder the heatsink with MosFET with a 1.5 mm gap to the PCB as detailed previously
  - the heatsink location pins should be soldered to the PCB to provide best stability
- T4:
  - The overcurrent bypass MosFET does not require any additional thermal pads when mounting to the small heatsink
  - Due to the thicker MosFET body it may be required to bend some of the heatsink fins to ~45° before it can be inserted
  - If a hole for screw mounting is available, secure part using M3 screw, nut and washers

### 3.2.3 High-Current OPET version

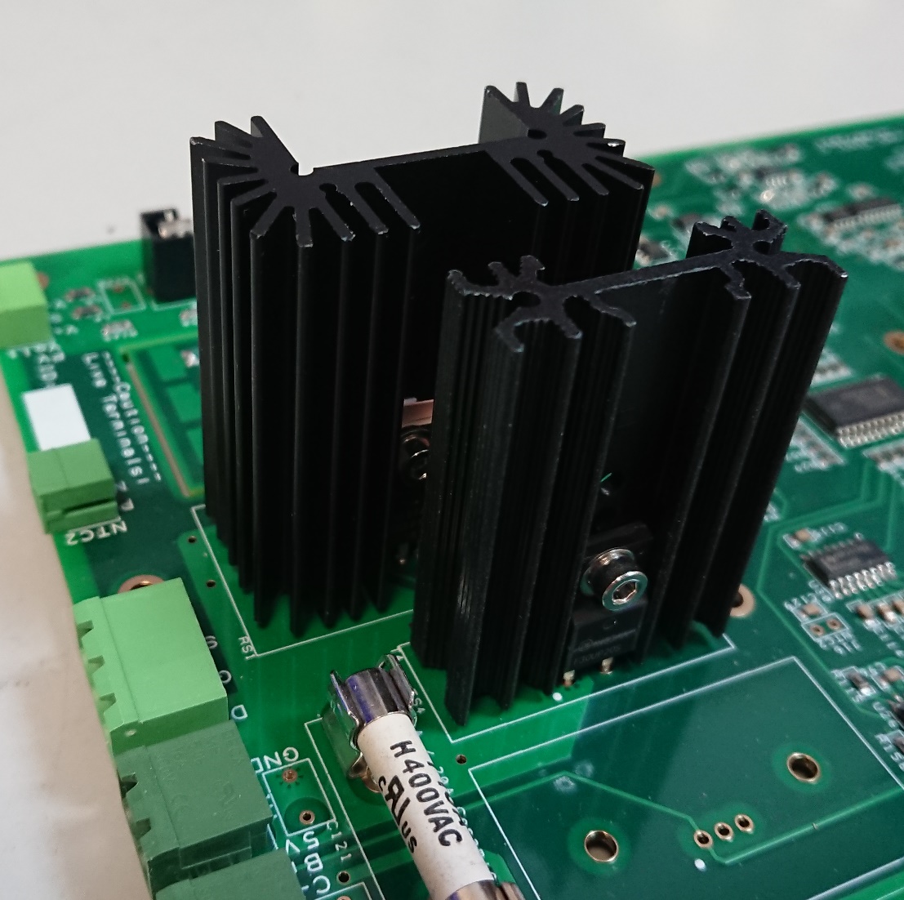
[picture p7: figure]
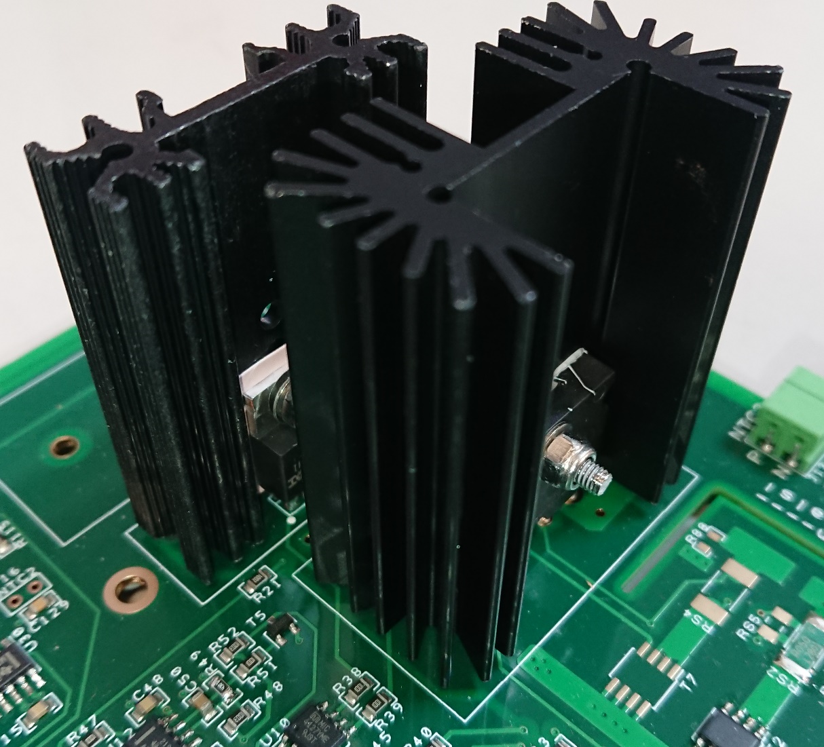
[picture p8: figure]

Figure 14: High-current OPET: Left: front side of T4 and RS1; Right: rear side of T4 and RS1; both heatsinks have a component screw mounted on both sides of the heatsink with electrically insulating pats and bushes or thermal paste, as detailed below

- T4:
  - The overcurrent bypass MosFET and bypass diode must be mounted together onto the heatsink
  - the MosFET must be mounted with a thermal pad as detailed at start of the main section
  - if the diode has an insulated body with a plastic base, it needs thermal paste to provide a good thermal contact to the heatsink
  - if the diode has a metal base, it needs an insulating pad and bush
  - solder the heatsink with components onto the PCB with a ~1.5 mm gap between the heatsink body and PCB
  - the heatsink location pins should be soldered to the PCB to provide best stability
- RS1:
  - The 15A shunt resistor needs to be mounted onto the heatsink together with the switching MosFET
  - To mount the components onto the heatsink a new screw hole must be drilled first
    - This needs to be 4 mm below the existing screw hole or 15mm from the bottom of the heatsink body excluding the locating pins
    - Deburr the newly drilled hole and make sure the contact area is flat and clean
    - The existing screw hole is too far from the edge for the short shunt resistor pins to reach through the PCB with a 1.5 mm gab between the PCB and heatsink
  - The MosFET must be mounted with an insulting pad as detailed at start of the main section
  - The Shunt resistor, if using standard BOM part, has a metal base that is insulated from all contact pins and hence should be mounted with high quality thermal paste
    - High quality meaning high thermal conductivity
  - the heatsink location pins should be soldered to the PCB to improve stability

OPET – Manual Introduction - 1

OPET – Manual Table of Contents

OPET – Manual PCB Assembly requirements and instructions - 3

OPET – PCB Design Notes Introduction - 1
